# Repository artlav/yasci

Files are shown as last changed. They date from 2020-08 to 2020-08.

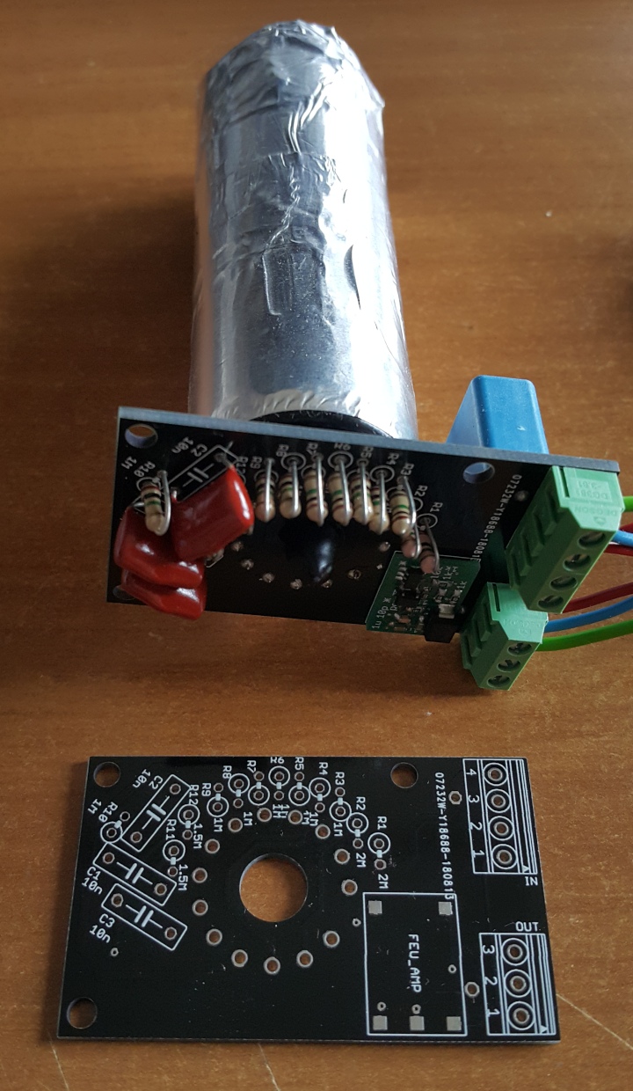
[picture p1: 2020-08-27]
doc/feu_85.jpg

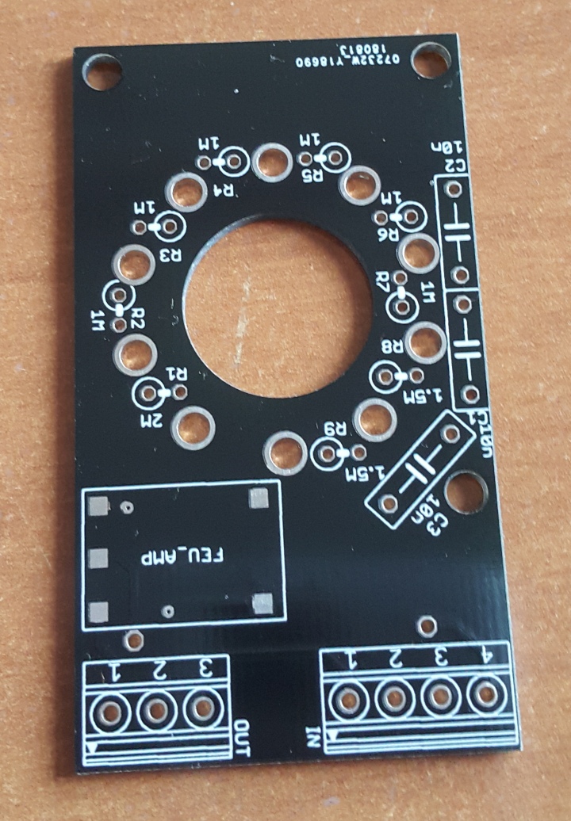
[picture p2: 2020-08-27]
doc/feu_35.jpg

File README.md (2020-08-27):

# Yet Another SCIntillation detector driver

A set of PCB designs to drive a PMT-based scintillation detector.  
Never got to finish it - the hardware is more or less done and largely tested, but failed to force myself to write the software/firmware.

## Power supply

 * A PMT needs around -1000V to work.
 * The logic stuff needs 5V.
 * The amplifier needs +5V and -5V.

This is a little brick that produces all of the above from 12V, using off-the-shelf converters to get +-5V and isolated 12V, boosting the isolated 12V to 250V, and voltage multiplying the 250V to 1000V.

## Amplifier

Takes the pulses from the PMT, amplifies and inverts them.  
I think i replaced MCP6021 with OPA172, for voltage limit reasons.

## ADC

An FPGA module with an ADC attached to it.  
Takes the analog output of the amplifier, digitizes it, processes/detects peaks, and saves it on a microsd card.  
The sync output is there to synchronize timings between several boards, i.e. for muon detection.

## Blank / FEU-85 / FEU-35

PMT boards, with amplifier mount point and resistor divider ladder.  
Pinouts for common ФЭУ-85 and ФЭУ-35 PMT tubes, as well as a blank one intended for an already-populated PMT module.

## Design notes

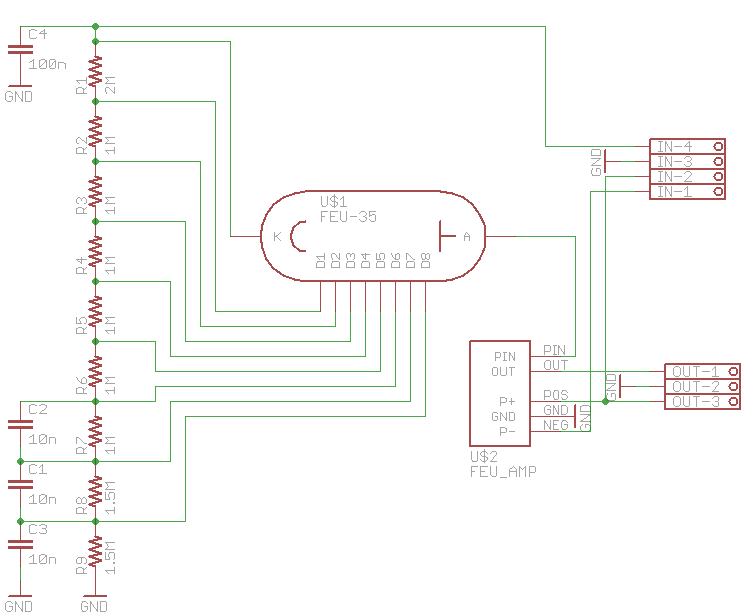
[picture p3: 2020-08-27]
doc/feu_35_sch.png

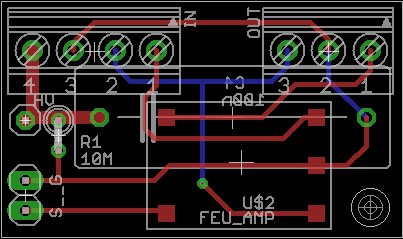
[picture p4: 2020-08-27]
doc/blank_pcb.png

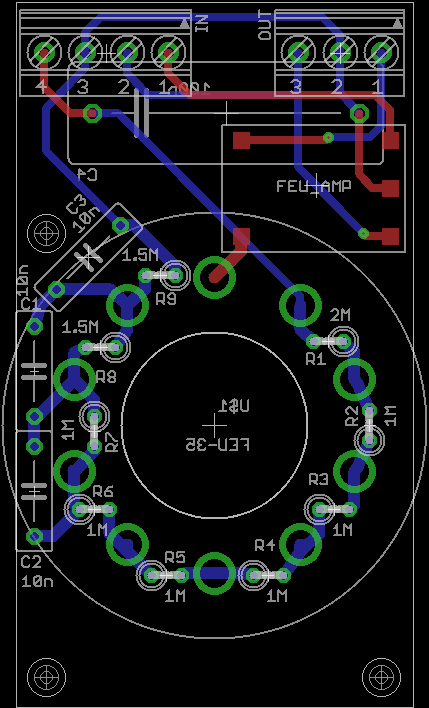
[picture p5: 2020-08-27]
doc/feu_35_pcb.png

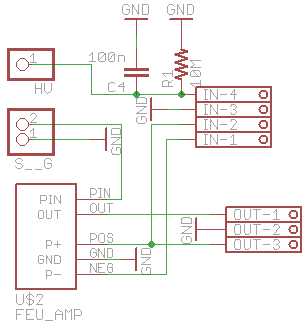
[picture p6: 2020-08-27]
doc/blank_sch.png

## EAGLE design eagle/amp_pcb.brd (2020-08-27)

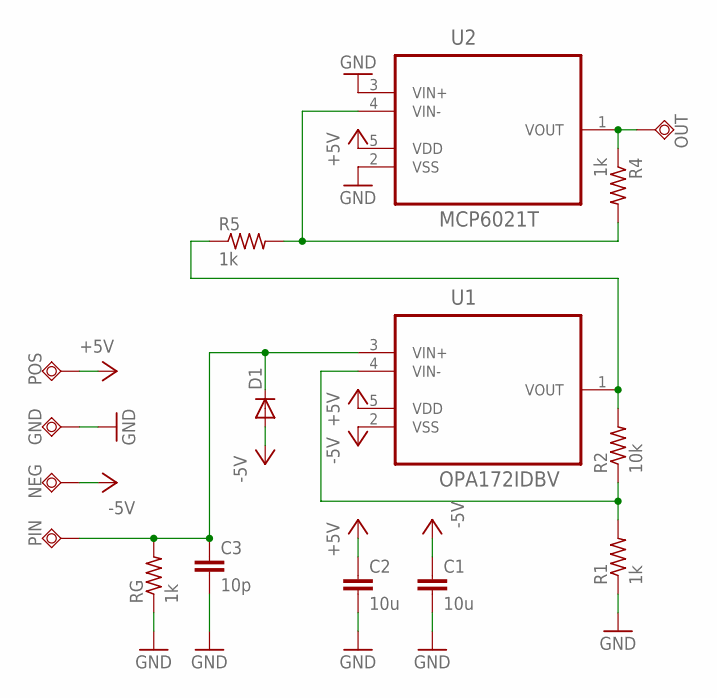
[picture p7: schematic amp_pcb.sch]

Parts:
C1, C2: 10u; C0603
C3: 10p; C0603
D1: DIODE-DO214AA; DO214AA
GND: TPSQTP15SQ; TP15SQ
NEG: TPSQTP15SQ; TP15SQ
OUT: TPSQTP15SQ; TP15SQ
PIN: TPSQTP15SQ; TP15SQ
POS: TPSQTP15SQ; TP15SQ
R1, R4, R5: 1k; R0603
R2: 10k; R0603
RG: 1k; R0603
U1: OPA172IDBV; SOT95P320X145-5N
U2: MCP6021T; SOT95P320X145-5N

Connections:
+5V: C2.1, POS.TP, U1.5 (VDD), U2.5 (VDD)
-5V: C1.1, D1.A, NEG.TP, U1.2 (VSS)
GND: C1.2, C2.2, C3.2, GND.TP, R1.1, RG.1, U2.2 (VSS), U2.3 (VIN+)
unnamed: R1.2, R2.1, U1.4 (VIN-)
unnamed: R2.2, R5.1, U1.1 (VOUT)
unnamed: C3.1, D1.C, PIN.TP, RG.2, U1.3 (VIN+)
unnamed: OUT.TP, R4.1, U2.1 (VOUT)
unnamed: R4.2, R5.2, U2.4 (VIN-)

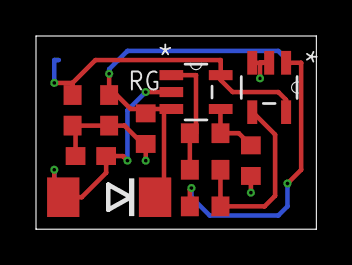
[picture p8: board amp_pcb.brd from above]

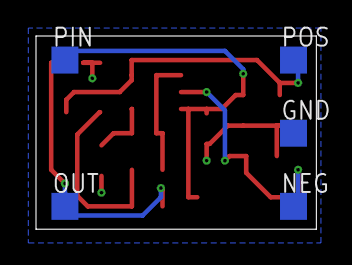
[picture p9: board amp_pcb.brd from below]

Board: 2 copper layers, 15.6 x 10.7 mm, 16 parts (5 on the bottom side), 8 nets.

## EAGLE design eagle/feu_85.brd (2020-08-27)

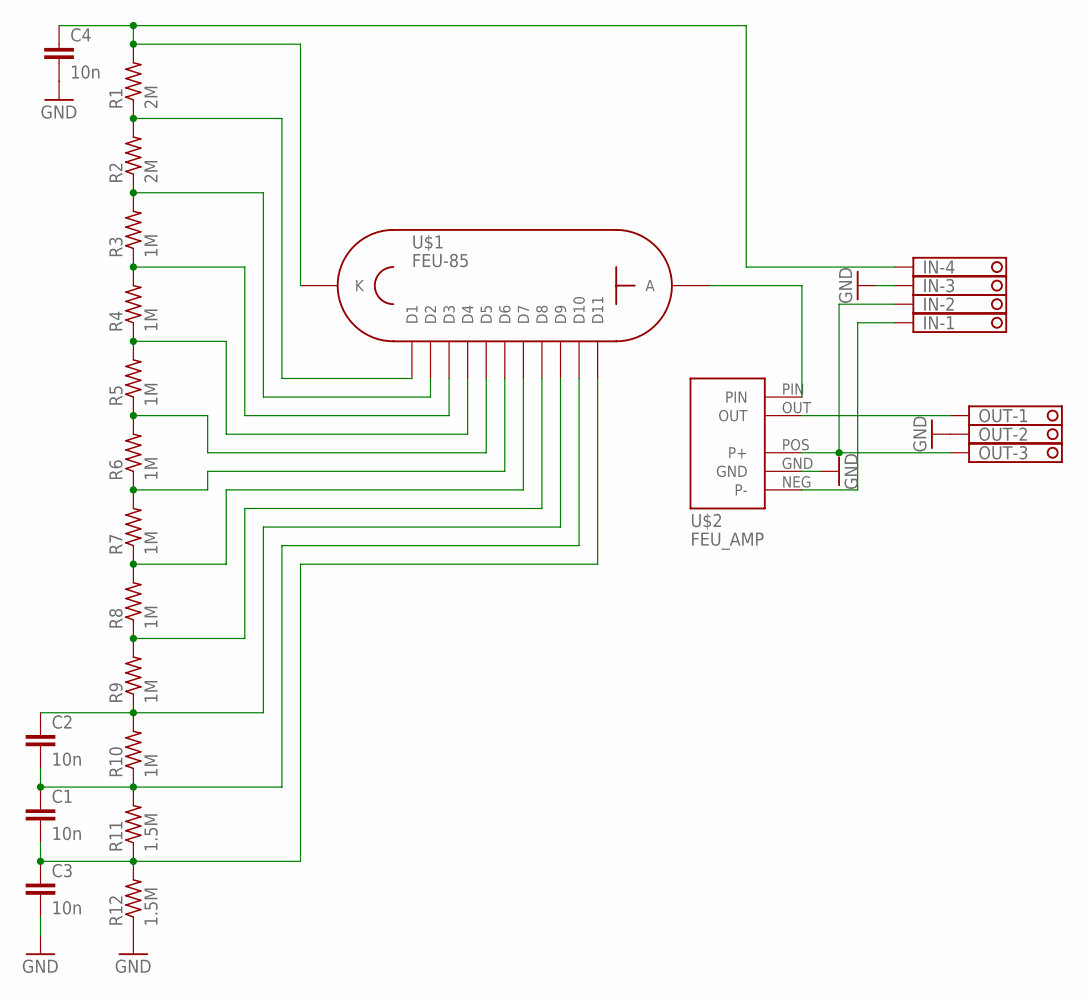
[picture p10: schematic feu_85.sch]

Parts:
C1, C2, C3: 10n; C075-032X103
C4: 10n; C225-087X268
IN: 1751264
OUT: 1751251
R1, R2: 2M; 0207/2V
R3, R4, R5, R6, R7, R8, R9, R10: 1M; 0207/2V
R11, R12: 1.5M; 0207/2V
U$1: FEU-85; PANEL_14
U$2: FEU_AMP

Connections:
GND: C3.2, C4.2, IN.3, OUT.2, R12.1, U$2.GND
unnamed: R1.1, R2.2, U$1.P$13 (D1)
unnamed: R3.1, R4.2, U$1.P$12 (D3)
unnamed: R4.1, R5.2, U$1.P$3 (D4)
unnamed: R5.1, R6.2, U$1.P$11 (D5)
unnamed: R6.1, R7.2, U$1.P$4 (D6)
unnamed: R7.1, R8.2, U$1.P$10 (D7)
unnamed: R8.1, R9.2, U$1.P$5 (D8)
unnamed: C2.1, R9.1, R10.2, U$1.P$9 (D9)
unnamed: OUT.1, U$2.OUT
unnamed: IN.2, OUT.3, U$2.POS (P+)
unnamed: R2.1, R3.2, U$1.P$2 (D2)
unnamed: C4.1, IN.4, R1.2, U$1.P$14 (K)
unnamed: C1.2, C3.1, R11.1, R12.2, U$1.P$8 (D11)
unnamed: C1.1, C2.2, R10.1, R11.2, U$1.P$6 (D10)
unnamed: U$1.P$7 (A), U$2.PIN
unnamed: IN.1, U$2.NEG (P-)

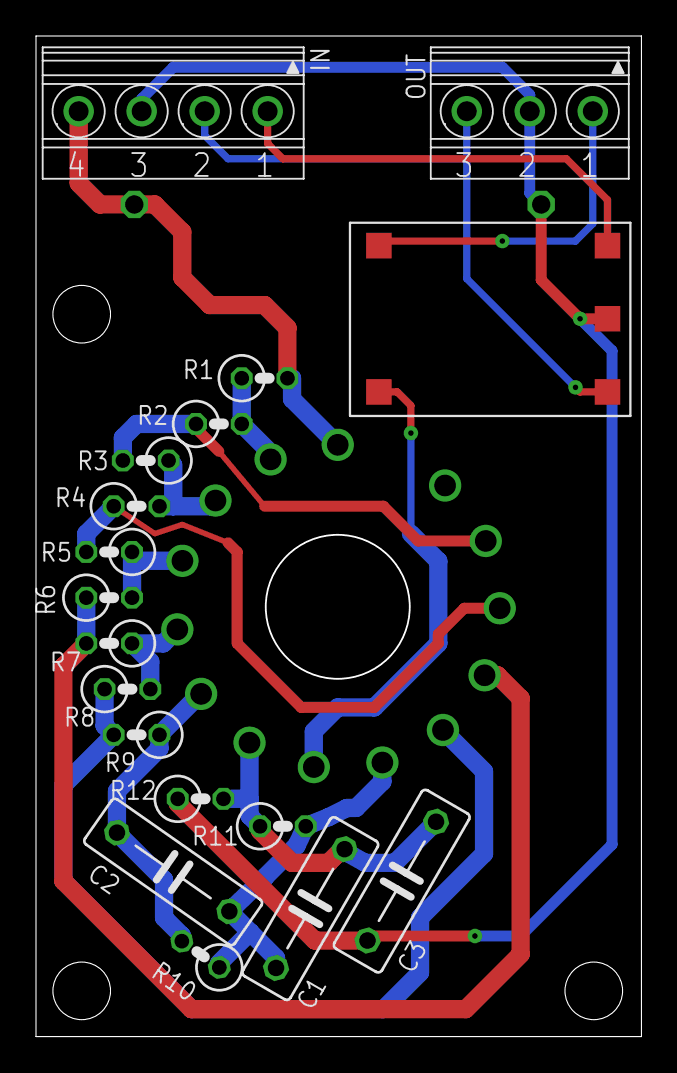
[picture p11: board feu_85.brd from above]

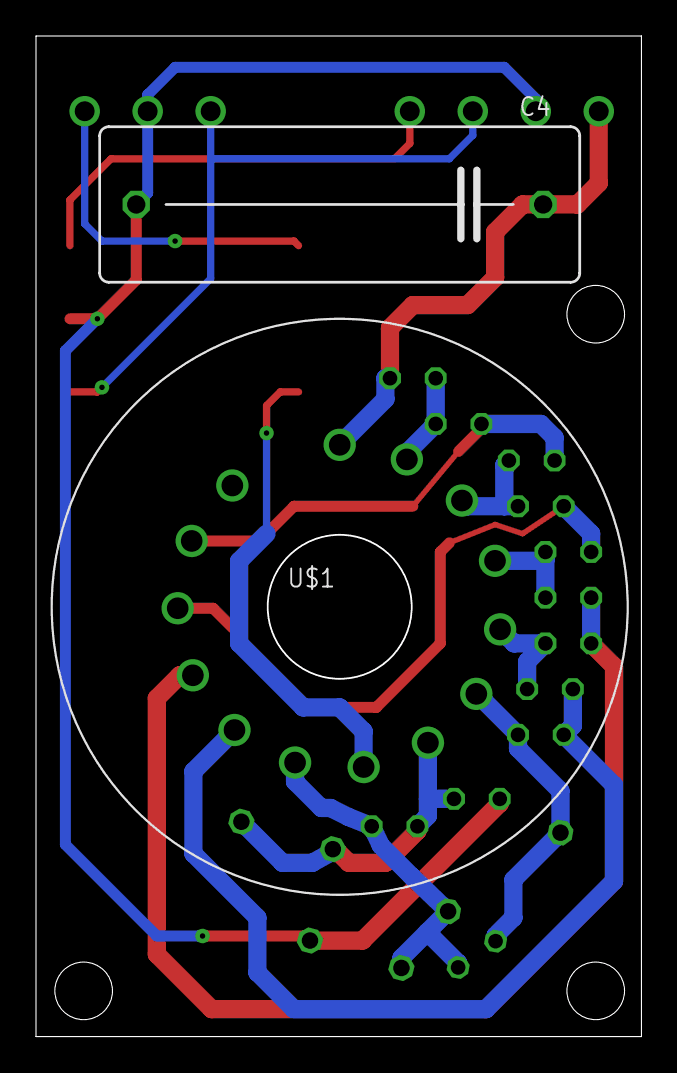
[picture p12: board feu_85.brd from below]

Board: 2 copper layers, 33.6 x 55.6 mm, 20 parts (2 on the bottom side), 17 nets.

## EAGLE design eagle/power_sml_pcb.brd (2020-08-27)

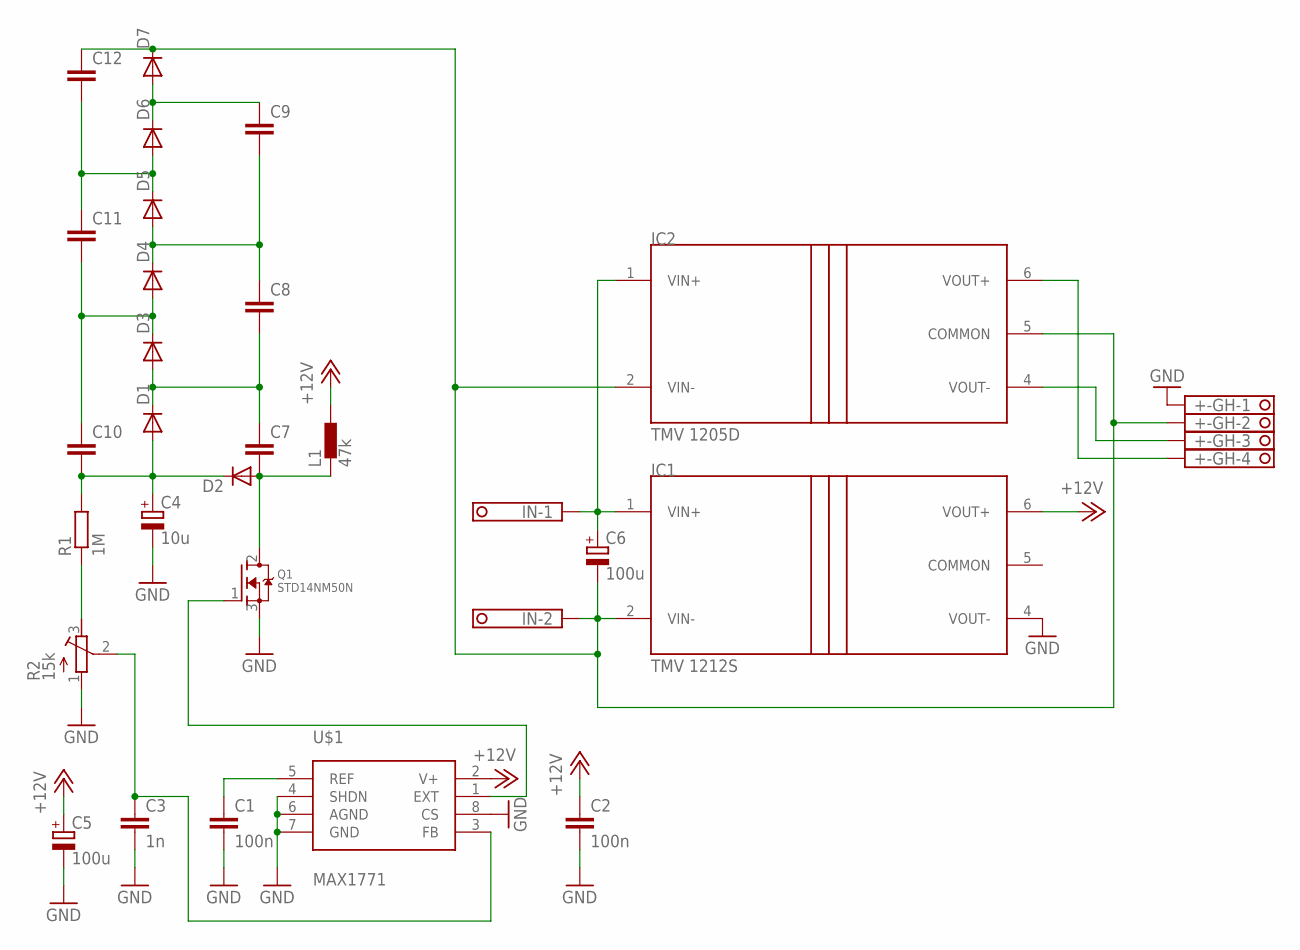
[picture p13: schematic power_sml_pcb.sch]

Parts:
+-GH: 1751264
C1, C2: 100n; C0603
C3: 1n; C0603
C4: 10u; E5-10,5
C5: 100u; SMC_C
C6: 100u; E2,5-6
C7, C8, C9, C10, C11, C12: C-EU102-054X133; C102-054X133
D1, D2, D3, D4, D5, D6, D7: DIODE-DO214AA; DO214AA
IC1: TMV 1212S; SIP7
IC2: TMV 1205D; SIP7
IN: 1751248
L1: 47k; DR1030
Q1: STD14NM50N; DPAK
R1: 1M; 0207/7
R2: 15k; RTRIM3296W
U$1: MAX1771; SOIC8

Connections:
+12V: C2.1, C5.+, IC1.6 (VOUT+), L1.2, U$1.2 (V+)
COMMON: IC1.5 (COMMON)
GND: +-GH.1, C1.2, C2.2, C3.2, C4.-, C5.-, IC1.4 (VOUT-), Q1.3 (S), R2.1 (E), U$1.4 (SHDN), U$1.6 (AGND), U$1.7 (GND), U$1.8 (CS)
unnamed: C1.1, U$1.5 (REF)
unnamed: C3.1, R2.2 (S), U$1.3 (FB)
unnamed: Q1.1 (G), U$1.1 (EXT)
unnamed: C7.2, D2.A, L1.1, Q1.2 (D)
unnamed: C4.+, C10.2, D1.A, D2.C, R1.2
unnamed: R1.1, R2.3 (A)
unnamed: C6.+, IC1.1 (VIN+), IC2.1 (VIN+), IN.1
unnamed: +-GH.4, IC2.6 (VOUT+)
unnamed: +-GH.3, IC2.4 (VOUT-)
unnamed: +-GH.2, C6.-, C12.1, D7.C, IC1.2 (VIN-), IC2.2 (VIN-), IC2.5 (COMMON), IN.2
unnamed: C7.1, C8.2, D1.C, D3.A
unnamed: C10.1, C11.2, D3.C, D4.A
unnamed: C8.1, C9.2, D4.C, D5.A
unnamed: C11.1, C12.2, D5.C, D6.A
unnamed: C9.1, D6.C, D7.A

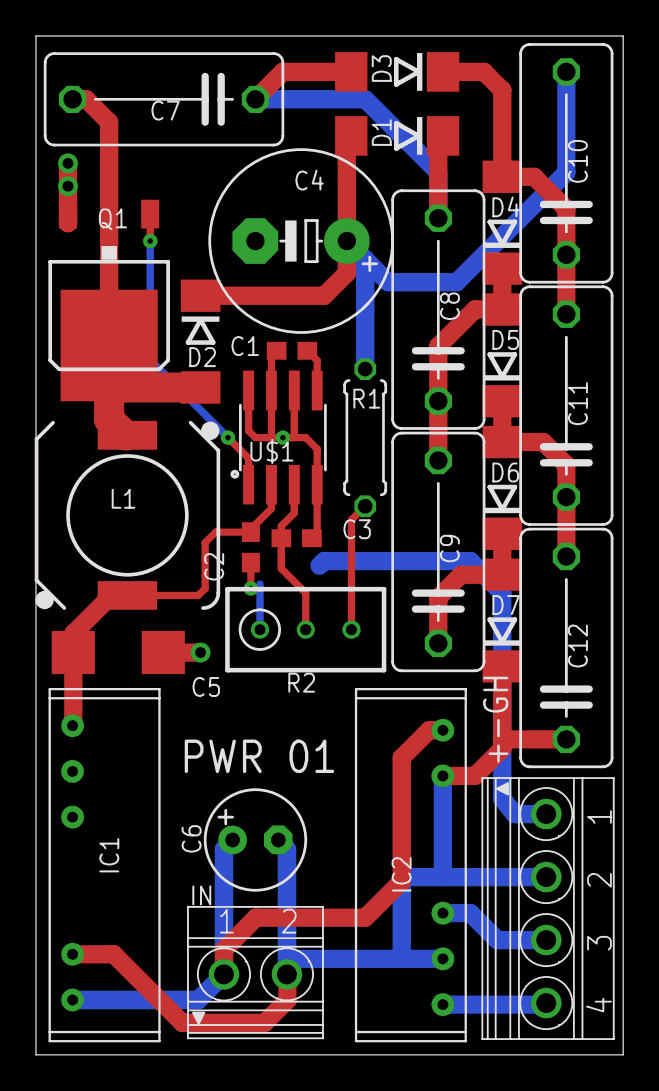
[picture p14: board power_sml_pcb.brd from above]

Board: 2 copper layers, 32.6 x 56.6 mm, 28 parts (0 on the bottom side), 17 nets.

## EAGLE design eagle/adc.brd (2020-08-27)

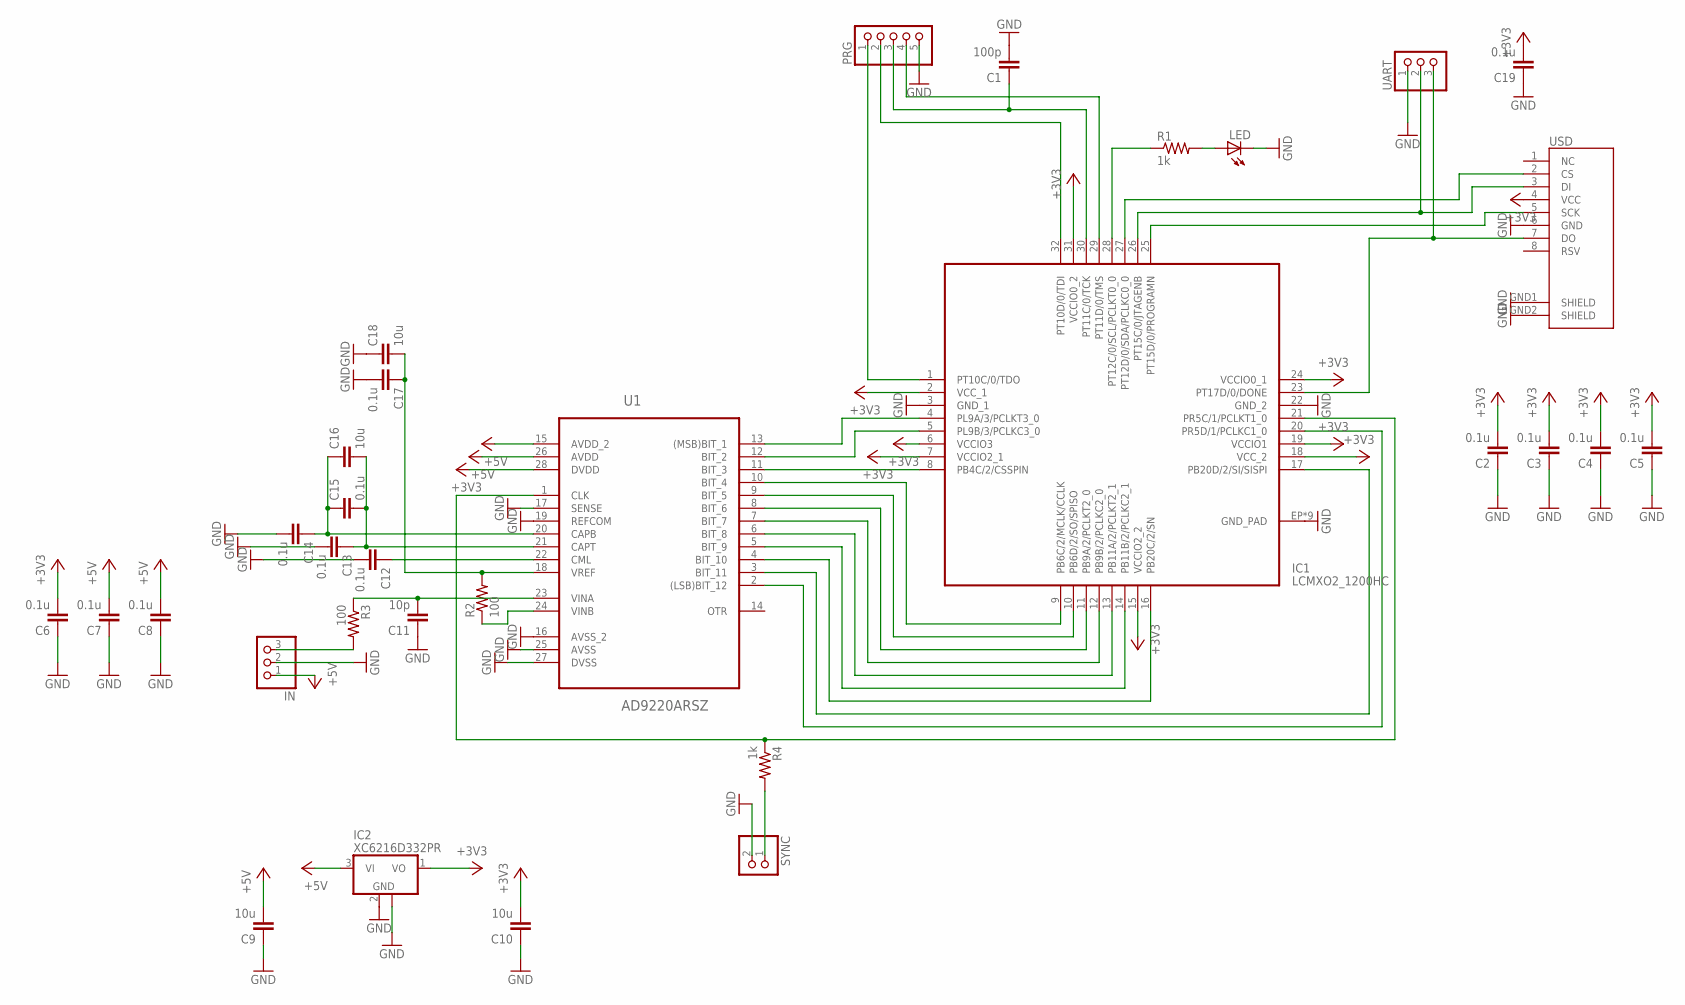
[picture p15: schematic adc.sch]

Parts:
C1: 100p; C0603
C2, C3, C4, C5, C6, C7, C8, C12, C13, C14, C15, C17, C19: 0.1u; C0603
C9, C10, C16, C18: 10u; C1206
C11: 10p; C0603
IC1: LCMXO2_1200HC; QFN32_5X5
IC2: XC6216D332PR; SOT89
IN: PINHD-1X3; 1X03
LED: LEDSML0805; SML0805
PRG: PINHD-1X5; 1X05
R1, R4: 1k; R0603
R2, R3: 100; R0603
SYNC: PINHD-1X2; 1X02
U1: AD9220ARSZ; SOP65P780X200-28N
UART: PINHD-1X3; 1X03
USD: USD-SOCKETUSD; USD-SOCKET-PP

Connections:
+3V3: C2.2, C3.2, C4.2, C5.2, C6.2, C10.2, C19.2, IC1.2 (VCC_1), IC1.6 (VCCIO3), IC1.7 (VCCIO2_1), IC1.15 (VCCIO2_2), IC1.18 (VCC_2), IC1.19 (VCCIO1), IC1.24 (VCCIO0_1), IC1.31 (VCCIO0_2), IC2.1 (VO), U1.28 (DVDD), USD.4 (VCC)
+5V: C7.2, C8.2, C9.2, IC2.3 (VI), IN.1, U1.15 (AVDD_2), U1.26 (AVDD)
GND: C1.2, C2.1, C3.1, C4.1, C5.1, C6.1, C7.1, C8.1, C9.1, C10.1, C11.1, C12.2, C13.2, C14.2, C17.2, C18.1, C19.1, IC1.3 (GND_1), IC1.22 (GND_2), IC1.EP (GND_PAD), IC1.EP1 (GND_PAD), IC1.EP2 (GND_PAD), IC1.EP3 (GND_PAD), IC1.EP4 (GND_PAD), IC1.EP5 (GND_PAD), IC1.EP6 (GND_PAD), IC1.EP7 (GND_PAD), IC1.PAD (GND_PAD), IC2.2 (GND), IC2.2@1 (GND), IN.2, LED.C, PRG.5, SYNC.2, U1.16 (AVSS_2), U1.17 (SENSE), U1.19 (REFCOM), U1.25 (AVSS), U1.27 (DVSS), UART.1, USD.6 (GND), USD.GND1 (SHIELD), USD.GND2 (SHIELD)
unnamed: IC1.4 (PL9A/3/PCLKT3_0), U1.13 ((MSB)BIT_1)
unnamed: IC1.5 (PL9B/3/PCLKC3_0), U1.12 (BIT_2)
unnamed: IC1.8 (PB4C/2/CSSPIN), U1.11 (BIT_3)
unnamed: IC1.9 (PB6C/2/MCLK/CCLK), U1.10 (BIT_4)
unnamed: IC1.10 (PB6D/2/SO/SPISO), U1.9 (BIT_5)
unnamed: IC1.11 (PB9A/2/PCLKT2_0), U1.8 (BIT_6)
unnamed: IC1.12 (PB9B/2/PCLKC2_0), U1.7 (BIT_7)
unnamed: IC1.13 (PB11A/2/PCLKT2_1), U1.6 (BIT_8)
unnamed: IC1.14 (PB11B/2/PCLKC2_1), U1.5 (BIT_9)
unnamed: IC1.16 (PB20C/2/SN), U1.4 (BIT_10)
unnamed: IC1.17 (PB20D/2/SI/SISPI), U1.3 (BIT_11)
unnamed: IC1.20 (PR5D/1/PCLKC1_0), U1.2 ((LSB)BIT_12)
unnamed: IC1.21 (PR5C/1/PCLKT1_0), R4.1, U1.1 (CLK)
unnamed: IC1.1 (PT10C/0/TDO), PRG.1
unnamed: IC1.32 (PT10D/0/TDI), PRG.2
unnamed: C1.1, IC1.30 (PT11C/0/TCK), PRG.3
unnamed: IC1.29 (PT11D/0/TMS), PRG.4
unnamed: IC1.23 (PT17D/0/DONE), UART.3, USD.7 (DO)
unnamed: IC1.25 (PT15D/0/PROGRAMN), USD.5 (SCK)
unnamed: IC1.26 (PT15C/0/JTAGENB), UART.2, USD.3 (DI)
unnamed: IC1.27 (PT12D/0/SDA/PCLKC0_0), USD.2 (CS)
unnamed: IC1.28 (PT12C/0/SCL/PCLKT0_0), R1.1
unnamed: LED.A, R1.2
unnamed: R2.1, U1.24 (VINB)
unnamed: C17.1, C18.2, R2.2, U1.18 (VREF)
unnamed: C11.2, R3.1, U1.23 (VINA)
unnamed: IN.3, R3.2
unnamed: C12.1, U1.22 (CML)
unnamed: C13.1, C15.2, C16.2, U1.21 (CAPT)
unnamed: C14.1, C15.1, C16.1, U1.20 (CAPB)
unnamed: R4.2, SYNC.1

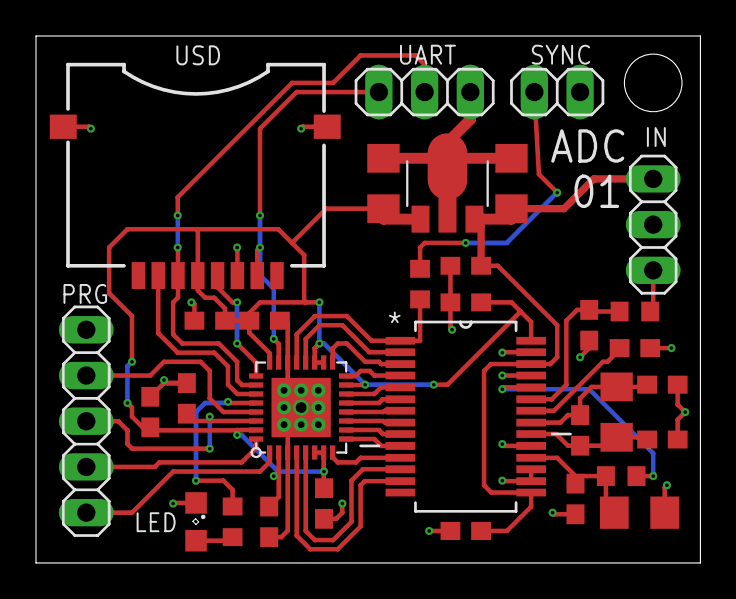
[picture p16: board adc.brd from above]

Board: 2 copper layers, 36.9 x 29.3 mm, 32 parts (0 on the bottom side), 34 nets.

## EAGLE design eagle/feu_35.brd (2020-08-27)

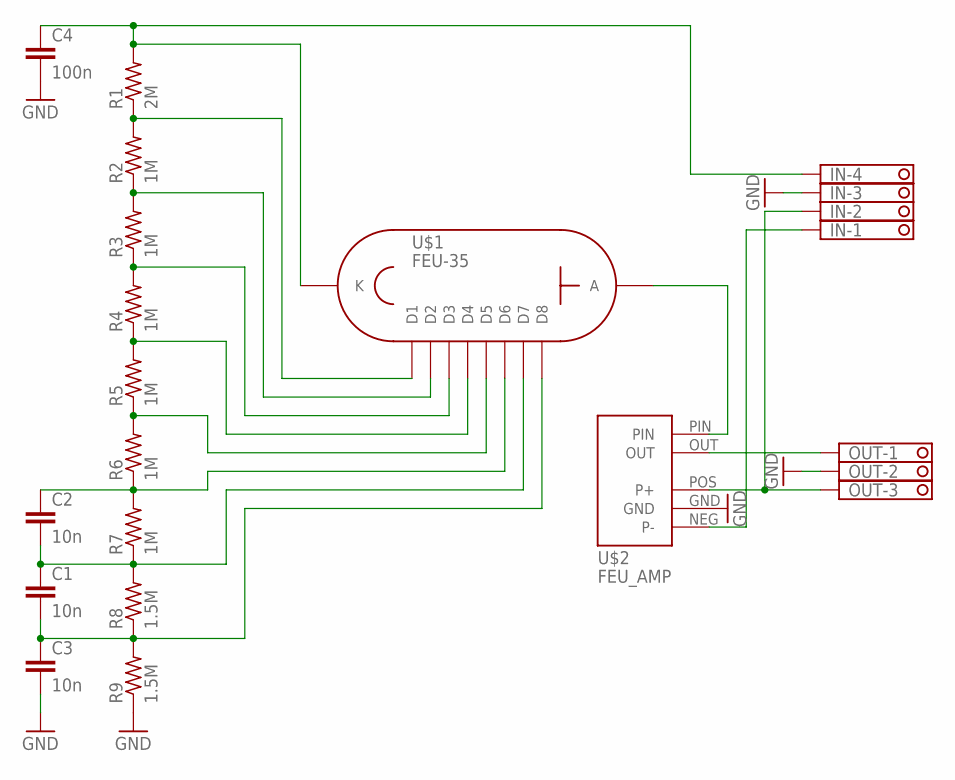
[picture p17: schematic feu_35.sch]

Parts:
C1, C2, C3: 10n; C075-032X103
C4: 100n; C225-087X268
IN: 1751264
OUT: 1751251
R1: 2M; 0207/2V
R2, R3, R4, R5, R6, R7: 1M; 0207/2V
R8, R9: 1.5M; 0207/2V
U$1: FEU-35; PANEL_10
U$2: FEU_AMP

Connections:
GND: C3.2, C4.2, IN.3, OUT.2, R9.1, U$2.GND
unnamed: R1.1, R2.2, U$1.P$2 (D1)
unnamed: R3.1, R4.2, U$1.P$4 (D3)
unnamed: R4.1, R5.2, U$1.P$5 (D4)
unnamed: R5.1, R6.2, U$1.P$6 (D5)
unnamed: C2.1, R6.1, R7.2, U$1.P$7 (D6)
unnamed: U$1.P$10 (A), U$2.PIN
unnamed: OUT.1, U$2.OUT
unnamed: IN.2, OUT.3, U$2.POS (P+)
unnamed: IN.1, U$2.NEG (P-)
unnamed: R2.1, R3.2, U$1.P$3 (D2)
unnamed: C4.1, IN.4, R1.2, U$1.P$1 (K)
unnamed: C1.2, C3.1, R8.1, R9.2, U$1.P$9 (D8)
unnamed: C1.1, C2.2, R7.1, R8.2, U$1.P$8 (D7)

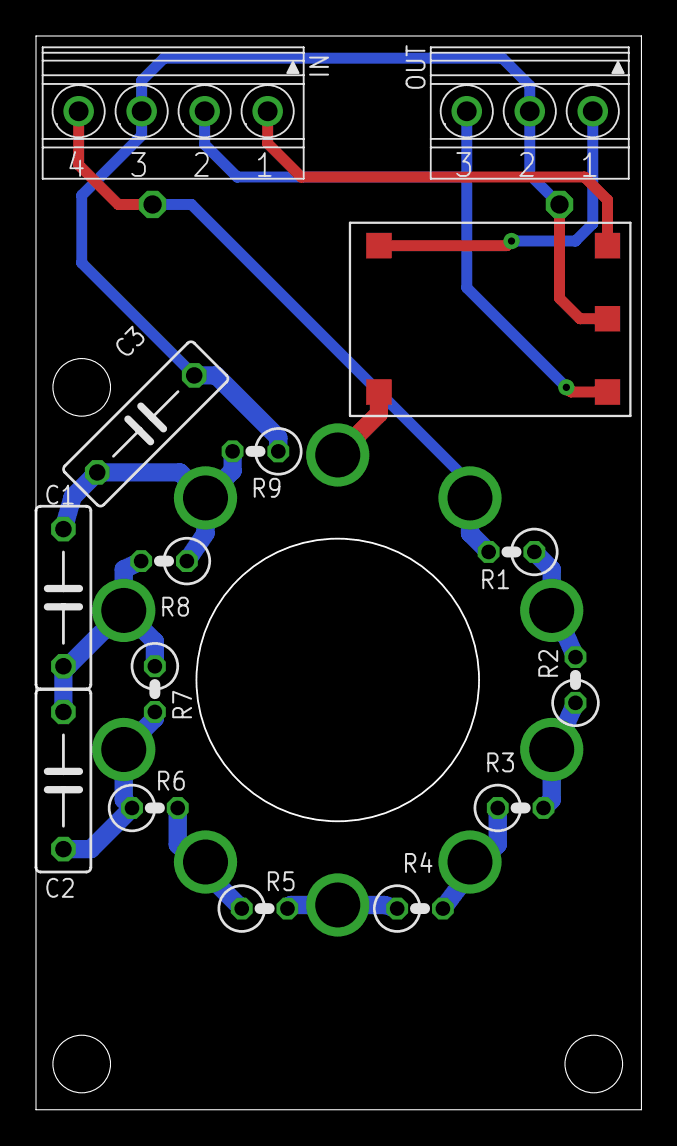
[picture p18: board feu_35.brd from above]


Board: 2 copper layers, 33.6 x 59.7 mm, 17 parts (2 on the bottom side), 14 nets.
